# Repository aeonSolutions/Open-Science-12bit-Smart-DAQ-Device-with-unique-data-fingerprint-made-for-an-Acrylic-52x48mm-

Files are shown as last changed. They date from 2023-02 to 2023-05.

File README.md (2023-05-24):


  
 
 

<a href="https://trackgit.com">
trackgit-views
</a>




[](https://www.buymeacoffee.com/migueltomas)

<p align="center">
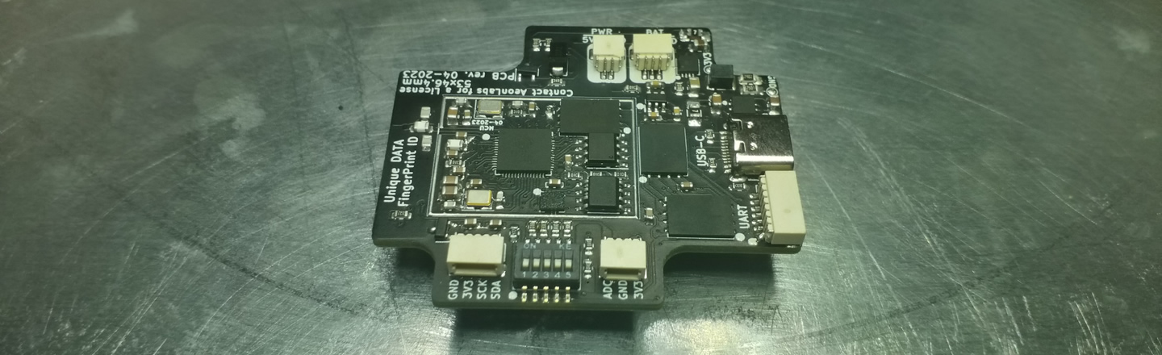
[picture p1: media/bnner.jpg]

</p>

<br>

[PCB-Prototyping-Catalogue](https://github.com/aeonSolutions/PCB-Prototyping-Catalogue)  >>  [Open Scientific Research](https://github.com/aeonSolutions/Open-Scientific-Research)  >>  12bit-Smart-DAQ-unique-data-fingerprint-made-for-an-Acrylic-52x48mm

# 12bit Smart DAQ Device with unique data fingerprint and a 1.69" TFT LCD made for an Acrylic 52x48mm  Enclosure

This is the repository for the 12bit Smart DAQ Device with unique data fingerprint able to do experimental data upload to any data repository. For detailed information head to the main project Wiki [here](https://github.com/aeonSolutions/openScience-Smart-DAQ-to-Upload-Live-Experimental-Data-to-a-Data-Repository/wiki). Thank you.

<br>

### 12bit Smart DAQ  Hardware Specifications
The hardware specifications for the 12bit PCB with dimensions of 52x46mm are the following:

- QFN 56 Dual Xtensa LX7 Core Processors running up to 240MHz
  -	RISC V ultra-low power co-processor
  - 512Kb RAM (PSRAM max 1 Gb);
  - 16Mb SOIC 8 NOR SPI Flash Memory (max 1Gb);
  - 2.4GHz ISM wireless connectivity;
  - Up to 118 12bit ADC Multiplexed DAQ channels;

<br>

- Onboard Storage:
  - 2x SPI Flash WSON-8 Chips for local storage upwards of 4Gbytes. 

<br>

- Authentication & Security:
  - SOIC-8 ATSHA204A SHA-256 high-security hardware authentication IC for secure and unique experimental data exchange

<br>

- Power management
  - DFN-6 AUR9718/ST1S09 high efficiency step-down 3.3V 1.5A DC converter;
  - CN3065 4.2V Lipo Battery Management System
  - USB-C connection for 5.0V 1.0A power supply from any power charger found on smartphones or tablets.
  - JST SH 2 pin 1.0mm for specific power supply applications (3.3V to 5.0V 1.0A DC)    

<br>

- Connectivity
  - 2.4GHz WIFI
  - Bluetooth & BLE
  - USB-C serial communication
  - JTAG debugger connector
  - Serial UART connector
  
<br>

- Onboard sensors:
  - DFN-8 AHT20; temperature sensor with a precision of 0.1 C;
  - DFN-8 AHT20 humidity sensor;
  - LGA-14 LSM6DS3 a 6-axis accelerometer and gyroscope;
  - TEMT6000 Luminosity Sensor;
  - SOT 23-3 reference voltage sensor;

<br>

- External connectivity for up to 118 sensors 12 to 16bit with onboard voltage reference analyzer with temperature compensation and automatic ADC calibration:
  -  1x I2C pin terminal connector (4 pin)
  -  1x ADC 12 to 16bit (with oversampling & digitization) digital terminal connector (3 pin)
  -  1x ADC Ohmmeter connection with 12 to 16bit (with oversampling & digitization) with manual scale selection via dip switch
 
<br>

- Display
  - 1.69" TFT LCD Display with a resolution of 320x280 px 

<br>

- Enclosure

This particular smart DAQ was designed to fit a well-known ABS enclosure commercially available on the internet. For instance [here](https://s.click.aliexpress.com/e/_DCKIAm1) on AliExpress. 

<br>

<br>

<p align="center">
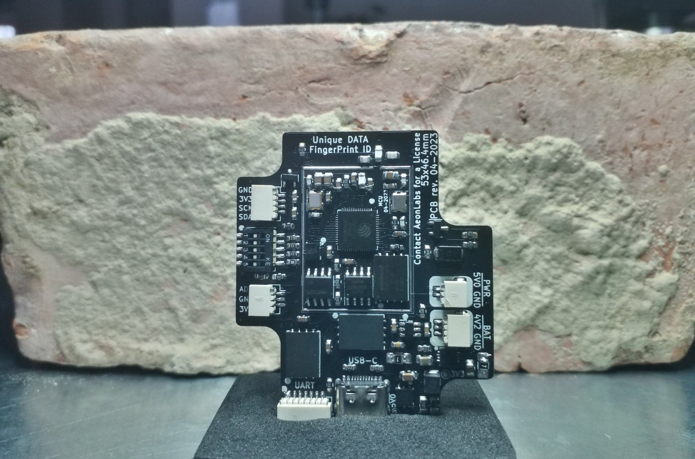
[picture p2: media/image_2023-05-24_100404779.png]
  
  
  
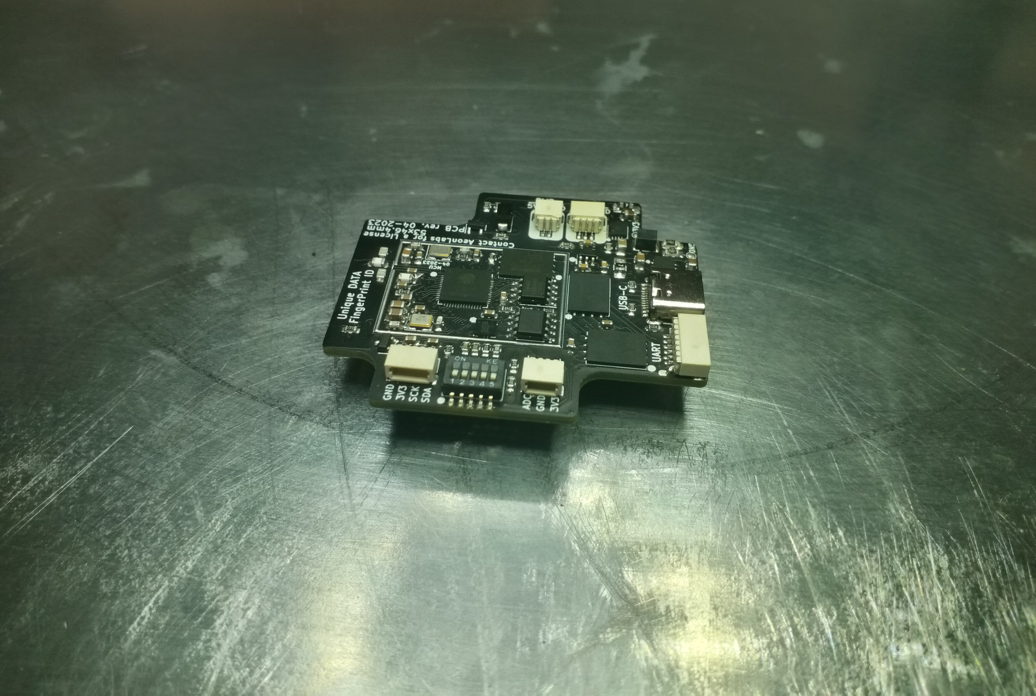
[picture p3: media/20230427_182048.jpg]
  
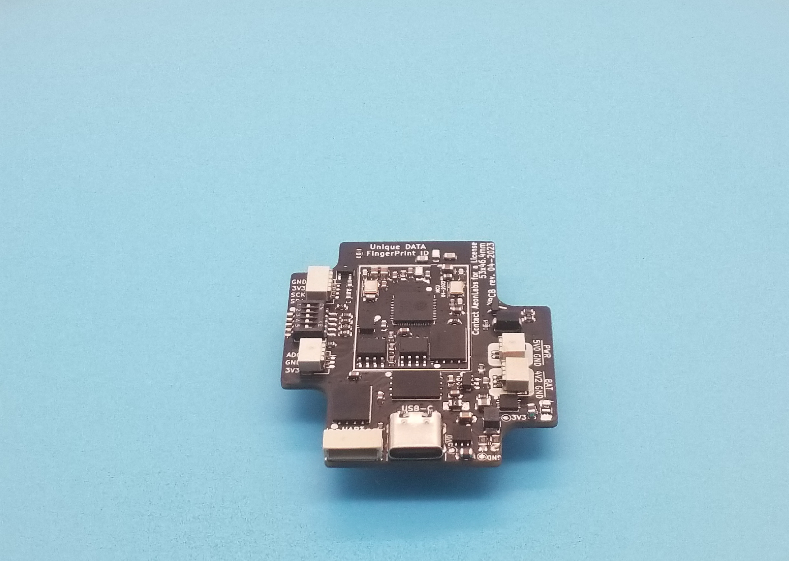
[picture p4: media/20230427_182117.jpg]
  
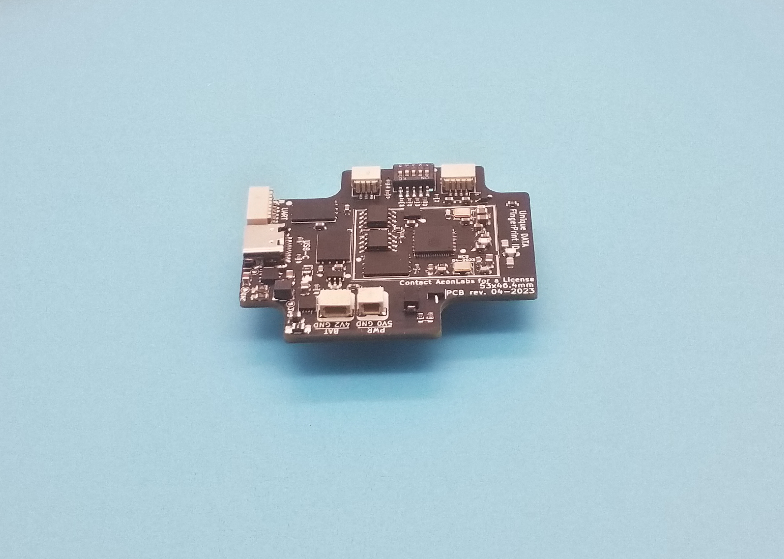
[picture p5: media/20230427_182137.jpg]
  
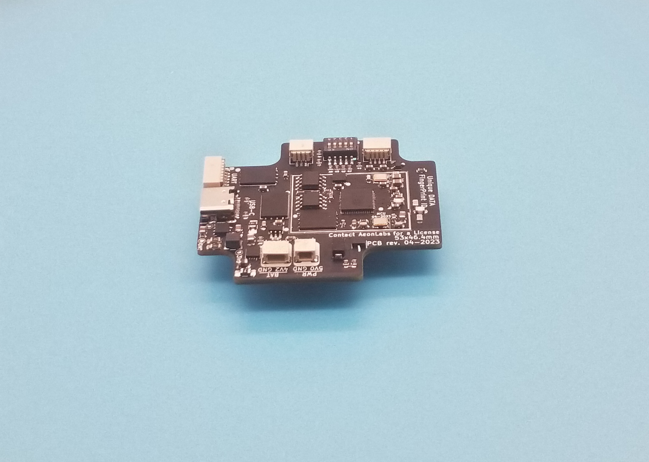
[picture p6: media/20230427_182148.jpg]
  
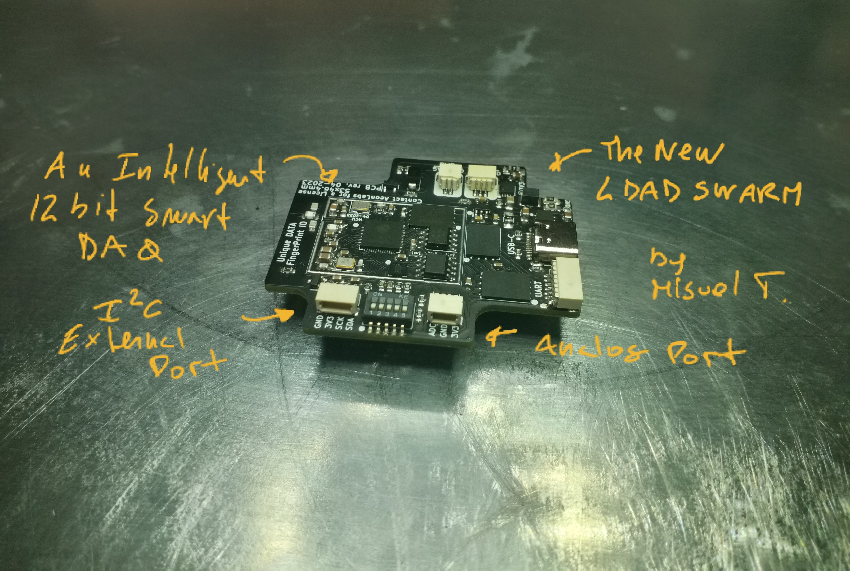
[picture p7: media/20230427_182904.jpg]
  
</p>

<br>

###  Status

Fully tested and working

 **Known PCB bugs [April 04-2023 pcb revision] :**
 
UART SH connector GND pin requires connection to GND on the PCB (easy fix. as it is exactly next to the GND pin). This only affects the onboard firmware upload UART port (the OEM firmware available here is able to do OTA updates using WIFI) .   

<br>

<p align="center">
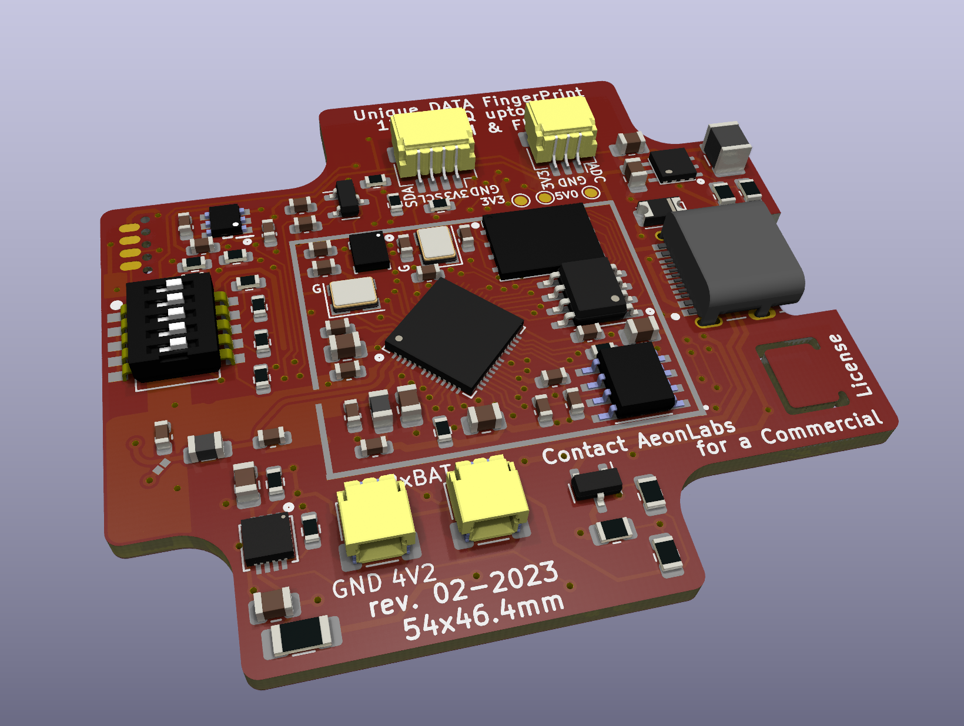
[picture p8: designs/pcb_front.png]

</p>

<p align="center">     
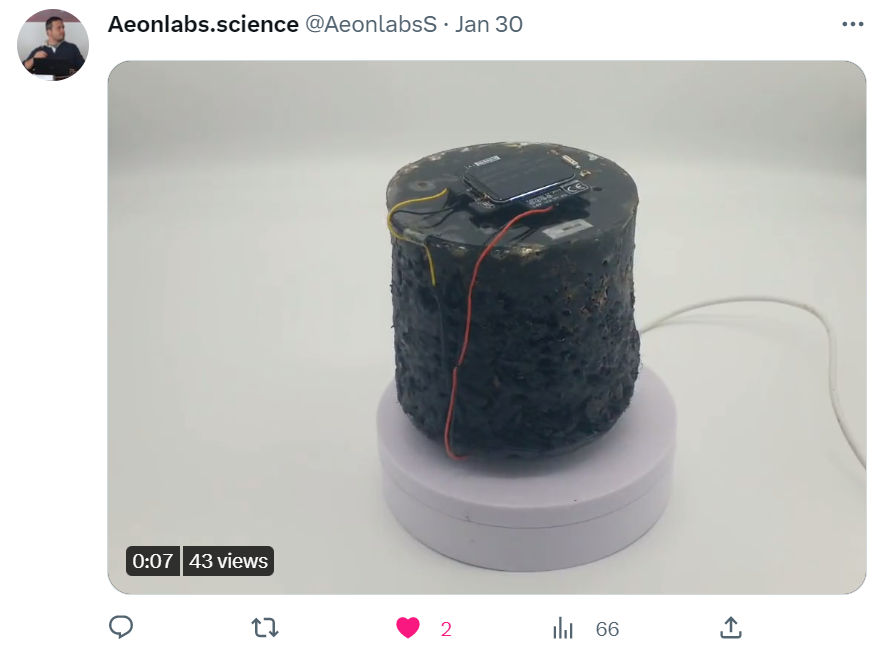
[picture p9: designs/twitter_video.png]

</p>

<br>

## What one additionally needs
- [USB to UART/USB TTL firmware burner for 5V and 3.3V MCUs ](https://github.com/aeonSolutions/PCB-Prototyping-Catalogue/blob/main/DIY-Maker/README.md) 

<br />
<br />

## Dataverse API C library

In paralell is being written a C library to expedite API integration on smart DAQ devices or elsewhere. Follow the link to its repository:

https://github.com/aeonSolutions/OpenScience-Dataverse-API-C-library

<p align="center">
  <a href="https://github.com/aeonSolutions/OpenScience-Dataverse-API-C-library">
   
 </a>
</p>

<br>

**Dataverse API in another coding language**

Goto dataverse.org for another coding language that best suits your coding style and needs. Currently there are client libraries for Python, Javascript, R, Java, and Julia that can be used to develop against Dataverse Software APIs

https://guides.dataverse.org/en/5.12/api/client-libraries.html

<br>
<br>

-----------------------------------------------------------------------------------

**Get a Notification on every PCB update**

| [](https://www.tindie.com/stores/aeonlabs/) | You can fill in your [email here (Google form)](https://docs.google.com/forms/d/e/1FAIpQLScErMgQYRdA-umvCjvTPPrCO7Lg1QYowTxb7vfa8cTfrcPEAA/viewform?usp=pp_url) and I'll send a reminder when a new PCB prototype is made available here or a new revision for an existing PCB. Stay tuned! |
|-------------|------|

<br />

**Be supportive of my dedication and work towards open hardware and buy me a cup of coffee. Links below. Above and on the side**

<br />
<br />

## Q&A WhatsApp/Telegram Groups
|  | Subscribe to the WhatsApp or Telegram channel to get latest information about any of this KiCad projects and get help. Or simply like this kind of projects and want to stay updated with the latest research ideas and prototypes during the day and week.   |
|-------------|------|

<br />
<br />

## Usefull Utilities 
|  | One can find here usefull utilities to use when designing and prototyping pcb electronics. For instance a simple excel spreadsheet with resistance divider finder compatible with all sold on [aliexpress](https://www.aliexpress.com/item/1005002792418456.html?spm=a2g0o.cart.0.0.22e538dayDM1YR&mp=1). Click on the Excel logo to the left to get them! |
|-------------|------|

<br />
<br />

## Author

You can get in touch with me on my LinkedIn Profile:

*Miguel Tomas* : 

You can also follow my GitHub Profile to stay updated about my latest projects: 

<br>

### Be supportive of my dedication and work towards open innovation & technology solutions and buy me a cup of coffee
The PCB Design Files I provide here for anyone to use are free. If you like this Smart Device or use it, please consider buying me a cup of coffee, a slice of pizza, or a book to help me study, eat and think new PCB design files.

<p align+"left">
<a href="https://www.buymeacoffee.com/migueltomas">
   
 </a>
<br>

</p>

<br />

### Make a donation on Paypal
Make a donation on PayPal and get a TAX refund*.

(http://paypal.me/mtpsilva)

<br>

### Support all these open hardware projects and become a Patreon  
Liked any of my PCB KiCad Designs? Help and Support my open work to all by becoming an LDAD Patreon.
In return, I will give a free PCB design in KiCad to all Patreon supporters. To learn more go to patreon.com. Link below.

(https://www.patreon.com/ldad)

<br />
<br />

______________________________________________________________________________________________________________________________
### License
2023 Creative Commons Attribution-NonCommercial-ShareAlike 4.0 International

https://creativecommons.org/licenses/by-nc-sa/4.0/

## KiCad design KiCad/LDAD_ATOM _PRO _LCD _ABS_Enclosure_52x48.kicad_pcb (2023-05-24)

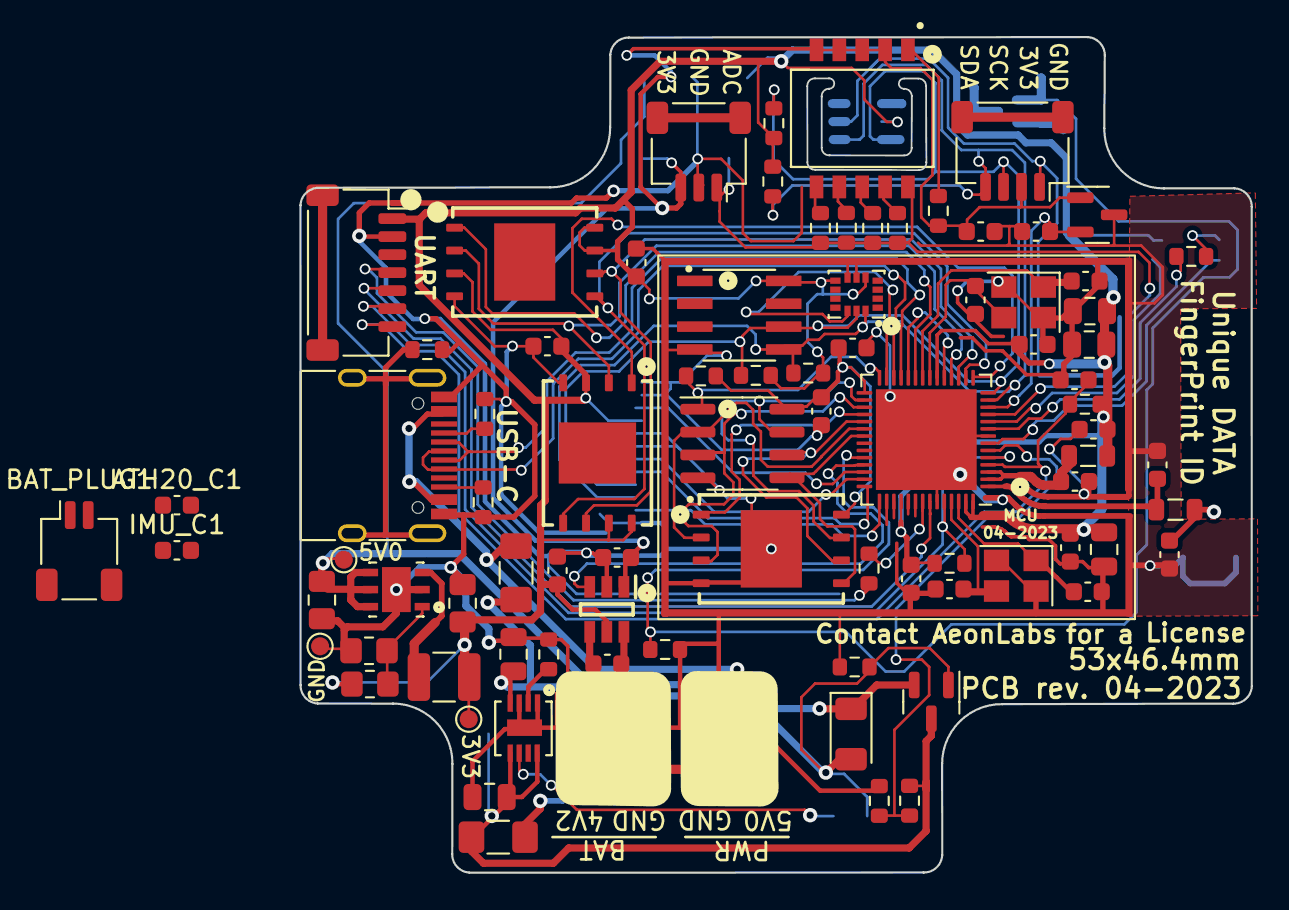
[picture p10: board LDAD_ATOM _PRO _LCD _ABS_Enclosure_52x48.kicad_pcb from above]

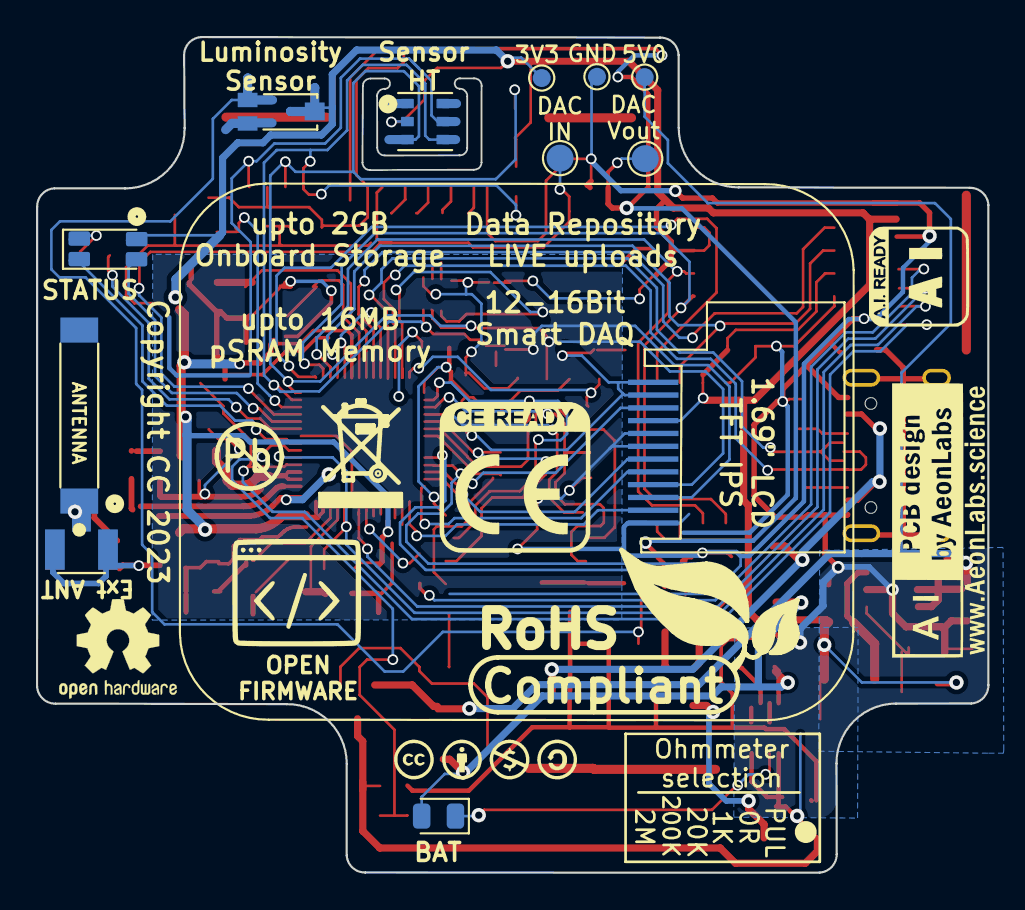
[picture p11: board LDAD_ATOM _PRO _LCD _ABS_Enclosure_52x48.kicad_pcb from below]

Board: 2 copper layers, 52.9 x 46.4 mm, 99 parts (13 on the bottom side), 66 nets.

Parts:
ATH20_C1: 100nF; C_0603_1608Metric
ATSHA_C1: 100nF; C_0603_1608Metric
AUR1: AUR9718x_DFN_3x3mm_6_pin; AUR9718 ST1S09 SON95P300X300X100-7N
AUR_C1: 22uF; C_0805_2012Metric_Pad1.18x1.45mm_HandSolder
AUR_C2: 4.7uF; C_0805_2012Metric_Pad1.18x1.45mm_HandSolder
AUR_R1: 24K; R_0805_2012Metric_Pad1.20x1.40mm_HandSolder
AUR_R2: 7k5; R_0805_2012Metric_Pad1.20x1.40mm_HandSolder
AUR_l1: 3.3uF; L_1210_3225Metric
BAT_FUSE1: Polyfuse; Fuse_1206_3216Metric_Pad1.42x1.75mm_HandSolder
BAT_PLUG1: Screw_Terminal_01x02; JST_SH_SM02B-SRSS-TB_1x02-1MP_P1.00mm_Horizontal
BAT_SENSE_R1, BAT_SENSE_R2: 100k; R_0603_1608Metric
CN3065_C2: 4.7uF; C_0805_2012Metric
CN3065_R1: 1K8; R_0603_1608Metric
CN3065_STDBY_LED1: LED; LED_0805_2012Metric
CN3965_C1: 22uF; C_0805_2012Metric
DIPSW1: Conn_02x05_Odd_Even; Dip Switch 5pin 1mm SW_DS05-127-2-06BK-SMT-TR
DIP_R1: 4k7; R_0603_1608Metric
DIP_R2: 1k; R_0603_1608Metric
DIP_R3: 20k; R_0603_1608Metric
DIP_R4: 200k; R_0603_1608Metric
DIP_R5: 2M; R_0603_1608Metric
DMP1045U_1: DMP1045U; SOT-23
DMP1045_R1: 10K; R_0603_1608Metric
DMP1045_SCHOT1: D_Schottky; D_1206_3216Metric
EPS1: ESP32-PSRAM_LY68L6400S; SOIC-8_3.9x4.9mm_P1.27mm
ESP32S1: ESP32-S3; QFN-56-1EP_7x7mm_P0.4mm_EP5.6x5.6mm
ESP32_SHIELD1: RFShield_OnePiece; ESP32-S3 GND Shield
ESP_FLASH1, ESP_FLASH2, ESP_FLASH3: W25Q128JVS; WSON8 FLASH SPI SON127P800X600X80-9N
E_DTR_R1: 10k; R_0603_1608Metric
E_LNA_ANT1: AN9520; 2.4ghZ WIFI ANTENNA AN9520_ANT2-SMD-9.5X2.1X1.0MM
E_LNA_ANT2: U.FL-R-SMT(01); RF Antenna IPEX SMD PCB HRS_U.FL-R-SMT(01)
E_LNA_C1, E_LNA_C2: 2.7pF; C_0603_1608Metric
E_LNA_l1: 1.8nH 5%; L_0805_2012Metric
E_RTS_C1: 100nF; C_0603_1608Metric
E_RTS_R1: 10k; R_0603_1608Metric
E_SPI_C1: 1uF 10% 50V; C_0603_1608Metric
E_SPI_C2: 100nF 10% 16V; C_0603_1608Metric
E_UART_TX_1: 499R; R_0603_1608Metric
E_VDDA_C1: 100nF; C_0603_1608Metric
E_VDDA_C2: 1uF 10% 50V; C_0805_2012Metric
E_VDD_3_C1, E_VDD_3_C2: 10uF 20% 6.3V; C_0805_2012Metric
E_VDD_3_C3, E_VDD_3_C4: 100nF 10% 16V; C_0603_1608Metric
E_VDD_CPU_C1: 100nF 10% 16V; C_0603_1608Metric
E_VDD_L1: 12nH 5%; L_0805_2012Metric
E_VDD_RTC_C1: 100nF 10% 16V; C_0603_1608Metric
E_XTAL32_1: 32.768Mhz 22pF+-10PPM; Crystal_SMD_3225-4Pin_3.2x2.5mm
E_XTAL32_C1, E_XTAL32_C2, E_XTAL40_C1, E_XTAL40_C2: 22pF 5% 50V; C_0603_1608Metric
E_XTAL40_1: 40Mhz 22pF+-10PPM; Crystal_SMD_3225-4Pin_3.2x2.5mm
ExtSW1: Conn_01x03_Female; JST_SH_SM03B-SRSS-TB_1x03-1MP_P1.00mm_Horizontal
ExtSWBAT_PLUG2: Conn_01x03_Female; JST_SH_SM03B-SRSS-TB_1x03-1MP_P1.00mm_Horizontal
HX1: HX4002; HX4002 SOT95 P280X125-6N
HX_C1, HX_C2, HX_C3: 2.2uF; C_0603_1608Metric
I2C_PLUG1: I2C6; JST_SH_SM04B-SRSS-TB_1x04-1MP_P1.00mm_Horizontal
I2C_SCL_R1, I2C_SDA_R1: 10k; R_0603_1608Metric
IMR1, IMR2: 10K; R_0603_1608Metric
IMU1: LSM6DS3; LSM6DS3 Motion Sensor PQFN50P300X250X86-14N
IMU_C1: 100nF; C_0603_1608Metric
J1: TYPE-C-31-M-12; USB_C_Receptacle_HRO_TYPE-C-31-M-12
JICSP1: Conn_01x07_Socket; JST_SH_SM07B-SRSS-TB_1x07-1MP_P1.00mm_Horizontal
LCD1: Conn_01x12_Male; 1,69 inch LCD IPS TFT
LED1: LED_GBRC; LED_1206_3210_RGB_Metric
LR1: 330R; R_0603_1608Metric
PSRAM_R1: 100K; R_0603_1608Metric
PWR_FUSE1: Polyfuse; Fuse_1206_3216Metric_Pad1.42x1.75mm_HandSolder
PWR_PLUG1: Screw_Terminal_01x02; JST_SH_SM02B-SRSS-TB_1x02-1MP_P1.00mm_Horizontal
SPI_STORAG_C1: 100nF; C_0603_1608Metric
Sign-PbFree: LOGO_PBFREE
Sign-RecycleBin: LOGO_RECYCLEBIN_1
Sign-RoHS: LOGO_ROHS_1
TMPR1: 10K; R_0603_1608Metric
TP1, TP1#2: VIN; TestPoint_Pad_D1.0mm
TP2, TP2#2: VOut; TestPoint_Pad_D1.0mm
TP3, TP3#2: GND; TestPoint_Pad_D1.0mm
U1: MCP1525-TT; SOT-23
U2: ATSHA204A-MAHDA-T; ATSHA204A Auth SOIC8
U3: Battery_charger_CN3065_QFN8; QFN8 3.1x2.9mm QFNn-8 3x3 SON80P400X400X100-9N
U4: AHT20; AHT20 HT Sensor PSON100P300X300X110-6N
U6: TEMT6000; TEMT6000-SEN
USB_PLUG_R1, USB_PLUG_R3: 5k1; R_0603_1608Metric
USB_PLYG_R2: 150K; R_0603_1608Metric
VOLTAGE_REF_C1, VOLTAGE_REF_C2: 100nF; C_0603_1608Metric

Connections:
3V3: ATH20_C1.2, ATSHA_C1.2, AUR_C1.1, AUR_R1.1, AUR_l1.1, ESP32S1.20 (VDD3P3_RTC), ESP32S1.46 (VDD3P3_CPU), ESP32S1.55 (VDDA), ESP32S1.56 (VDDA), ESP_FLASH2.3 (IO2), ESP_FLASH2.7 (IO3), ESP_FLASH2.8 (VCC), ESP_FLASH3.3 (IO2), ESP_FLASH3.7 (IO3), ESP_FLASH3.8 (VCC), E_DTR_R1.1, E_RTS_R1.1, E_VDDA_C1.2, E_VDDA_C2.2, E_VDD_3_C1.1, E_VDD_3_C2.1, E_VDD_3_C3.1, E_VDD_CPU_C1.1, E_VDD_L1.1, E_VDD_RTC_C1.1, HX1.5 (VIN), HX_C3.2, I2C_SCL_R1.1, I2C_SDA_R1.2, IMR1.1, IMR2.1, IMU1.5 (VDDIO), IMU1.8 (VDD), IMU_C1.2, JICSP1.1, LCD1.4, LED1.4 (K), SPI_STORAG_C1.2, TP2.1, TP2#2.1, U2.8 (VCC), U4.2 (VDD), U6.COLLECTOR
3V3_PLUG: DIPSW1.3, DIPSW1.5, DIPSW1.7, DIPSW1.9, DIP_R1.2, ExtSW1.3, HX1.1 (VOUT), HX_C1.1, I2C_PLUG1.2, U1.1 (Vin), VOLTAGE_REF_C1.2
ADC_IN_IO04: DIPSW1.2, DIP_R2.1, DIP_R3.1, DIP_R4.1, DIP_R5.1, ESP32S1.11 (GPIO6/ADC1_CH5), ExtSW1.1
BAT_SENSE_IO21: BAT_SENSE_R1.1, BAT_SENSE_R2.2, ESP32S1.6 (GPIO1/ADC1_CH0)
CHIP_EN: ESP32S1.4 (CHIP_PU/RESET), E_RTS_C1.2, E_RTS_R1.2, JICSP1.7
DAC_CALIBRATION: ESP32S1.19 (GPIO14/ADC2_CH3), ESP32S1.24 (GPIO18/ADC2_CH7/DAC_1)
ESP_GPIO0_BOOT-DTR: ESP32S1.5 (GPIO0/BOOT), ESP32S1.52 (GPIO46), E_DTR_R1.2, JICSP1.6
FSPICLK_IO12: ESP32S1.17 (GPIO12/ADC2_CH1), ESP_FLASH2.6 (CLK), ESP_FLASH3.6 (CLK)
GND: ATH20_C1.1, ATSHA_C1.1, AUR1.2 (GND), AUR1.7 (GND), AUR_C1.2, AUR_C2.2, AUR_R2.2, BAT_SENSE_R1.2, CN3065_C2.1, CN3065_R1.1, CN3965_C1.1, DMP1045_R1.2, EPS1.4 (VSS), ESP32S1.8 (GPIO3/ADC1_CH2), ESP32S1.51 (GPIO45), ESP32S1.57 (GND), ESP32_SHIELD1.1 (Shield), ESP_FLASH1.4 (GND), ESP_FLASH1.9 (GND), ESP_FLASH2.4 (GND), ESP_FLASH3.4 (GND), E_LNA_ANT2.1 (GND), E_LNA_ANT2.2 (GND), E_LNA_C1.2, E_LNA_C2.2, E_RTS_C1.1, E_SPI_C1.2, E_SPI_C2.2, E_VDDA_C1.1, E_VDDA_C2.1, E_VDD_3_C1.2, E_VDD_3_C2.2, E_VDD_3_C3.2, E_VDD_3_C4.2, E_VDD_CPU_C1.2, E_VDD_RTC_C1.2, E_XTAL32_1.2, E_XTAL32_1.4, E_XTAL32_C1.2, E_XTAL32_C2.2, E_XTAL40_1.2, E_XTAL40_1.4, E_XTAL40_C1.2, E_XTAL40_C2.2, ExtSW1.2, ExtSWBAT_PLUG2.3, HX1.2 (GND), HX_C1.2, HX_C3.1, I2C_PLUG1.1, IMU1.6 (GND), IMU1.7 (GND), IMU_C1.1, J1.B1, J1.B12 (A12), JICSP1.2, LCD1.1, LCD1.2, LCD1.5, LCD1.6, LCD1.12, PWR_PLUG1.1, SPI_STORAG_C1.1, TMPR1.1, TP3.1, TP3#2.1, U1.3 (Vss), U2.4 (GND), U3.1 (V_Temp), U3.3 (GND), U3.9 (GND), U4.5 (GND), USB_PLUG_R1.2, USB_PLUG_R3.2, USB_PLYG_R2.2, VOLTAGE_REF_C1.1, VOLTAGE_REF_C2.1
GPIO8_I2C_SDA: ESP32S1.13 (GPIO8/ADC1_CH7), I2C_PLUG1.4, I2C_SDA_R1.1, IMR1.2, IMU1.14 (SDA), LCD1.10, U2.5 (SDA), U4.4 (SDA)
GPIO9_I2C_SCL: ESP32S1.14 (GPIO9/ADC1_CH8), I2C_PLUG1.3, I2C_SCL_R1.2, IMR2.2, IMU1.13 (SCL), LCD1.9, U2.6 (SCL), U4.3 (SCL)
IMU_CS_IO21: ESP32S1.27 (GPIO21), IMU1.12 (CS)
LCD2_CS_IO37: ESP32S1.42 (GPIO37), LCD1.8
LCD2_DC_IO36: ESP32S1.41 (GPIO36), LCD1.7
LCD2_LED_IO35: ESP32S1.40 (GPIO35), LCD1.3
LCD2_RST_IO38: ESP32S1.43 (GPIO38), LCD1.11
LED_B_IO05: ESP32S1.10 (GPIO5/ADC1_CH4), LED1.2 (BA)
LED_G_IO02: ESP32S1.7 (GPIO2/ADC1_CH1), LED1.1 (GA)
LED_R_IO04: ESP32S1.9 (GPIO4/ADC1_CH3), LR1.1
unnamed: AUR1.1 (FB), AUR_R1.2, AUR_R2.1
unnamed: AUR1.3 (SW), AUR_l1.2
unnamed: DIPSW1.1, DIP_R1.1
unnamed: DIPSW1.4, DIP_R2.2
unnamed: DIPSW1.6, DIP_R3.2
unnamed: DIPSW1.8, DIP_R4.2
unnamed: DIPSW1.10, DIP_R5.2
unnamed: ESP32S1.21 (GPIO15/ADC2_CH4/XTAL_32K_P), E_XTAL32_1.3, E_XTAL32_C1.1
unnamed: ESP32S1.22 (GPIO16/ADC2_CH5/XTAL_32K_N), E_XTAL32_1.1, E_XTAL32_C2.1
unnamed: ESP32S1.1 (LNA_IN/RF), E_LNA_C2.1, E_LNA_l1.2
unnamed: ESP32S1.49 (U0TXD/PROG/GPIO43), E_UART_TX_1.2
unnamed: ESP32S1.2 (VDD3P3), ESP32S1.3 (VDD3P3), E_VDD_3_C4.1, E_VDD_L1.2
unnamed: ESP32S1.53 (XTAL_N), E_XTAL40_1.3, E_XTAL40_C2.1
unnamed: ESP32S1.54 (XTAL_P), E_XTAL40_1.1, E_XTAL40_C1.1
unnamed: E_LNA_ANT1.1, E_LNA_ANT2.3 (SIG), E_LNA_C1.1, E_LNA_l1.1
unnamed: HX1.6 (C+), HX_C2.1
unnamed: HX1.4 (C-), HX_C2.2
unnamed: J1.A5 (CC1), USB_PLUG_R3.1
unnamed: J1.B5 (CC2), USB_PLUG_R1.1
unnamed: J1.S1 (SHIELD), USB_PLYG_R2.1
unnamed: LED1.3 (RA), LR1.2
unnamed: CN3065_R1.2, U3.2 (I_SET)
PLUG_PWR_3V3_EN_IO38: ESP32S1.39 (GPIO34), HX1.3 (EN)
RXD0: ESP32S1.50 (U0RXD/PROG/GPIO44), JICSP1.5
SPICLK: EPS1.6 (SCLK), ESP32S1.33 (SPICLK/GPIO30), ESP_FLASH1.6 (CLK)
SPICS0: ESP32S1.32 (SPICS0/GPIO29), ESP_FLASH1.1 (~CS)
SPICS1: EPS1.1 (~CE), ESP32S1.28 (SPI_CS1/GPIO26), PSRAM_R1.1
SPID: EPS1.5 (SiO0), ESP32S1.35 (SPID/GPIO32), ESP_FLASH1.5 (DI(IO0))
SPIHD: EPS1.7 (SIO3), ESP32S1.30 (SPIHD/GPIO27), ESP_FLASH1.7 (IO3)
SPIQ: EPS1.2 (SIO1), ESP32S1.34 (SPIQ/GPIO31), ESP_FLASH1.2 (DO(IO1))
SPIWP: EPS1.3 (SIO2), ESP32S1.31 (SPIWP/GPIO28), ESP_FLASH1.3 (IO2)
STDBY_LED_G: CN3065_STDBY_LED1.1 (K), U3.6 (LED_DONE)
STORAGE_2_CS_IO17: ESP32S1.23 (GPIO17/ADC2_CH6/DAC_2), ESP_FLASH2.1 (~CS)
STORAGE_CS_IO10: ESP32S1.15 (GPIO10/ADC1_CH9), ESP_FLASH3.1 (~CS)
STORAGE_MISO_SPIQ_IO13: ESP32S1.18 (GPIO13/ADC2_CH2), ESP_FLASH2.2 (DO(IO1)), ESP_FLASH3.2 (DO(IO1))
STORAGE_MOSI_SPID_IO11: ESP32S1.16 (GPIO11/ADC2_CH0), ESP_FLASH2.5 (DI(IO0)), ESP_FLASH3.5 (DI(IO0))
TEMT6000_IO33: ESP32S1.38 (GPIO33), TMPR1.2, U6.EMITTER
TXD0: E_UART_TX_1.1, JICSP1.4
USB_5V0: CN3065_STDBY_LED1.2 (A), CN3965_C1.2, DMP1045U_1.1, DMP1045_R1.1, DMP1045_SCHOT1.2 (A), PWR_FUSE1.1, U3.4 (VIN)
USB_5V0F: J1.A9, J1.B4, PWR_FUSE1.2, PWR_PLUG1.2
USB_D+: ESP32S1.26 (GPIO20/USB_D+/ADC2_CH9), J1.A6 (DP1), J1.B6 (DP2)
USB_D-: ESP32S1.25 (GPIO19/USB_D-/ADC2_CH8), J1.A7 (DN1), J1.B7 (DN2)
VDD_SPI: EPS1.8 (VCC), ESP32S1.29 (VDD_SPI), ESP_FLASH1.8 (VCC), E_SPI_C1.1, E_SPI_C2.1, PSRAM_R1.2
VIN: AUR1.4 (VIN_SW), AUR1.5 (VIN_A), AUR1.6 (EN), AUR_C2.1, DMP1045U_1.2, DMP1045_SCHOT1.1 (K), TP1.1, TP1#2.1
VIN_BAT: BAT_FUSE1.1, BAT_SENSE_R2.1, CN3065_C2.2, DMP1045U_1.3, U3.5 (BAT+), U3.8 (FB)
VIN_BATF: BAT_FUSE1.2, ExtSWBAT_PLUG2.1
VOLTAGE_REF_IO07: ESP32S1.12 (GPIO7/ADC1_CH6), U1.2 (Vout), VOLTAGE_REF_C2.2

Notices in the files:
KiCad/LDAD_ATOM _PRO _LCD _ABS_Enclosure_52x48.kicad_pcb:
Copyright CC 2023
